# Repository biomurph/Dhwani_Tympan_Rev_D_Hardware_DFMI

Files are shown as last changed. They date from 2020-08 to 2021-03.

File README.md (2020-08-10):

D_Tympan_DFMI_1.0 consisits of PCB design files catering to the requirements of Indian PCB Manufacturers. 

The following are the changes done in the PCB design files (.pcb file):  

	1.Four layered board with power/gnd planes as follows:
		Top Cu - GND plane   
		Second layer(In. Cu 1) - None  
		Third layer(In. Cu 2) - 3.3 V power plane  
		Bottom Cu - GND plane  
	2.Details about vias:  
		Through hole vias - 0.6mm/0.4mm  
		Blind vias ( In. Cu 2 - B. Cu) - 0.45mm/ 0.15mm  
	3. Changes in component placement:  
		R20, R23 - Moved from B. Cu to F. Cu layer  
		C14, C20, C21, C22,C34 - Moved from B. Cu to F. Cu layer

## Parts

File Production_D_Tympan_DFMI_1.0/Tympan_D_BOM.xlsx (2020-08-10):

Item | Reference | Package | Quantity | Value | Manufacturer | Part Number | Notes
1 | BT1 | 4UCON-0217-20519 | 1 | 4UCON-20519 | 4UCON | 20519 | Consigned by Solutions
2 | C1,C3,C5,C7,C10,C14,C16,C18,C28,C29,C42 | C_0402 | 11 | 0.1uF | TDK Corporation | C1005X7R1H104K050BB
3 | C2,C8,C12,C13,C23,C24,C25,C26,C27,C32,C33,C37,C39 | C_0402 | 13 | 2.2uF | Murata | GRT155C71A225KE13D
4 | C30,C31 | C_0402 | 2 | 10nF | Yageo | AC0402KPX7R9BB103
5 | C35 | C_0402 | 1 | 4.7uF | TDK Corporation | C1005X5R1A475K050BC
6 | C4,C6,C11,C15 | C_0402 | 4 | 10uF | Murata | GRM155C80J106ME11J
7 | C40 | C_0402 | 1 | 15pF | Wurth | 885012005008
8 | C41 | C_0402 | 1 | 22nF | Wurth | 885012205014
9 | C9,C17,C19,C20,C21,C22,C34 | C_0402 | 7 | 1uF | Murata | GRM155C81C105KE15D
10 | CONN1 | MOLEX_47571-0001 | 1 | 8_PIN_microSD | Molex | 47571-0001
11 | D1 | ABHB1608S | 1 | 2 color LED | Everlight | 18-225SURSYGC/S530-A4/E4/TR8
12 | D2 | C_1206 | 1 | LED Red | Lite-On | LTST-C150EKT
13 | D3 | C_1206 | 1 | LED Amber | Lite-On | LTST-C150AKT
14 | D4,D5 | ACDBA340-HF | 2 | Shottkey | Comchip | ACDBA340-HF
15 | D6 | CLMVB-FKA-CFHEHLCBB7a363 | 1 | Led_RGB_CA | Cree | CLMVB-FKA-CFHEHLCBB7a363
16 | F1 | C_1206 | 1 | FUSE | Bell Fuse | C1Q 1
17 | IC1 | BGA-144-1mm | 1 | ARM | NXP | MK66FX1M0VMD18
18 | IC2 | QFN-16-1EP_3x3mm_Pitch0.5mm | 1 | MKL02Z32VFG4 | PJRC | IC_MKL02Z32_QFN16 | Consigned by Solutions
19 | IC3 | BC127 | 1 | BC127 | Sierra Wireless | BC127-1103383
20 | J1 | SJ-3523-SMT-TR | 1 | Phone Out | CUI Inc | SJ-3523-SMT-TR
21 | J2 | SJ-3524-SMT-TR | 1 | Mic In | CUI Inc | SJ-3524-SMT-TR-PI
22 | L1,L2 | C_0402 | 2 | 600R | TDK Corporation | MMZ1005S601HT000
23 | L3 | C_0603 | 1 | 1K | Murata | BLM18KG102SH1D
24 | MIC2,MIC1 | SPM0687LR5H-1 | 2 | MEMS Microphone | Knowles | SPM0687LR5H-1
25 | P1 | 10118193_microUSB | 1 | USB_OTG | Amphenol | 10118193-0001LF
26 | P3,P4,P5,P2 | Pin_Header_Straight_1x06_Pitch2.54mm | 4 | CONN_01X06 | Samtec | SSW-106-01-G-S
27 | P6 | Pin_Header_Straight_1x03_Pitch2.00mm | 1 | DNP | DNP | DNP | DNP
28 | R12,R13 | C_0603 | 2 | 0R | Vishay Dale | CRCW06030000Z0EA
29 | R14,R17 | C_0603 | 2 | DNP | DNP | DNP | DNP
30 | R15,R16 | C_0603 | 2 | 2.2K | Yageo | RC0603FR-072K2L
31 | R18,R21 | R_0402 | 2 | 240R | Yageo | RC0402JR-07240RL
32 | R19,R20,R32,R33,R1,R11 | R_0402 | 6 | 1K | Vishay Dale | CRCW04021K00FKED
33 | R23 | R_0402 | 1 | 100K | Vishay Dale | CRCW0402100KFKED
34 | R25,R34,R35,R36 | R_0402 | 4 | 470R | Yageo | RC0402FR-07470RL
35 | R30,R31 | R_0402 | 2 | 10K | Yageo | RC0402FR-0710KL
36 | R6,R2,R3,R4,R5,R7,R9,R10,R26,R27 | R_0402 | 10 | 33R | Yageo | RC0402FR-0733RL
37 | R8 | R_0402 | 1 | 2.2K | Yageo | RC0402JR-0722KL
38 | RV1 | Pin_Header_Straight_1x03_Pitch2.54mm | 1 | POT | Bourns | 3352T-1-103L
39 | SW1 | CL-SB-22A | 1 | Slide Switch | Nidec Copal | CL-SB-22A-11T
40 | SW2 | PTS810 | 1 | TACT_SWITCH | C&K | PTS810 SJK 250 SMTR LFS
41 | U1 | SOT-23-5 | 1 | 3V3 Regulator | Diodes Inc | AP2210K-3.3TRG1
42 | U2 | UQFN-40-1EP_5x5mm_Pitch0.4mm | 1 | CODEC | Texas Instrument | TLV320AIC3206IRSBT
43 | U3 | SOT-353_SC-70-5 | 1 | Analog Switch IC | Texas Instrument | TS5A3166DCKR
44 | U4 | SOT-23-5 | 1 | 1V8 Regulator | Texas Instrument | LP5907MFX-1.8/NOPB
45 | U5 | SOT-23-5 | 1 | LiPo Charge IC | Microchip | MCP73831T-2DCI/OT
46 | Y1 | LFXTAL009678 | 1 | 32.768kHz | IQD | LFXTAL009678Reel
47 | Y2 | FA_238_16.0000MB_K3 | 1 | 16MHz | Epson | FA_238_16.0000MB_K3

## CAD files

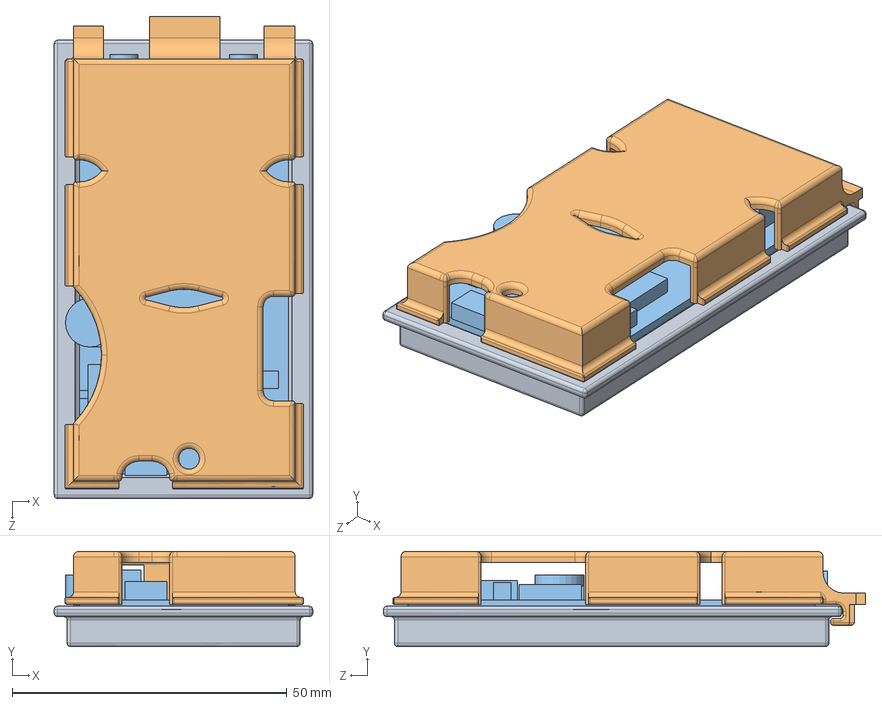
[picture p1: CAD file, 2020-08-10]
Enclosure/Enclosure_01/Tympan D Enclosure Assembly.SLDASM
47.0 x 17.4 x 87.7 mm
Joel Enclosure Bottom
Joel Enclosure Top
Chip's Chip

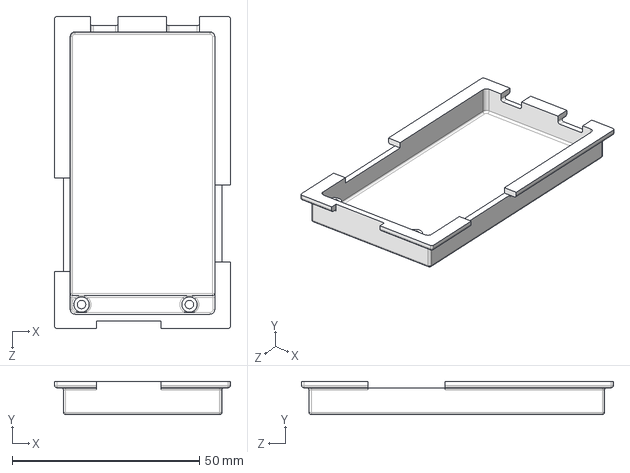
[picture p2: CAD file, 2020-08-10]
DFMI_1.0/Enclosure/Enclosure_01/Tympan D Enclosure Bottom.STEP
47.0 x 8.89 x 83.4 mm

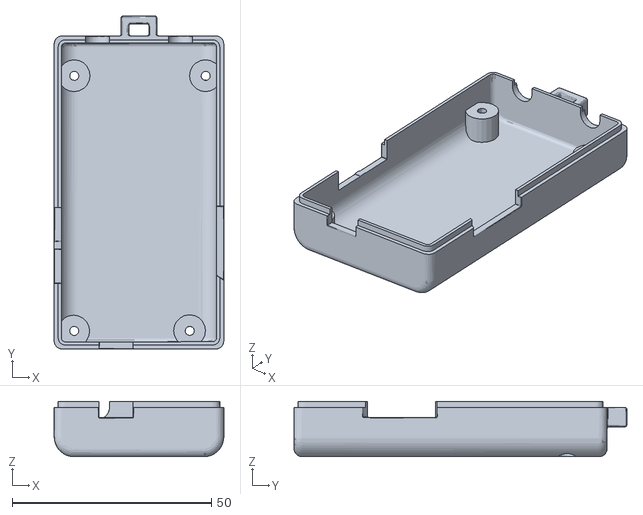
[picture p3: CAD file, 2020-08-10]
Enclosure/Enclosure_02/Tympan RevD Case Bottom.stl
42.6 x 83.6 x 13.9

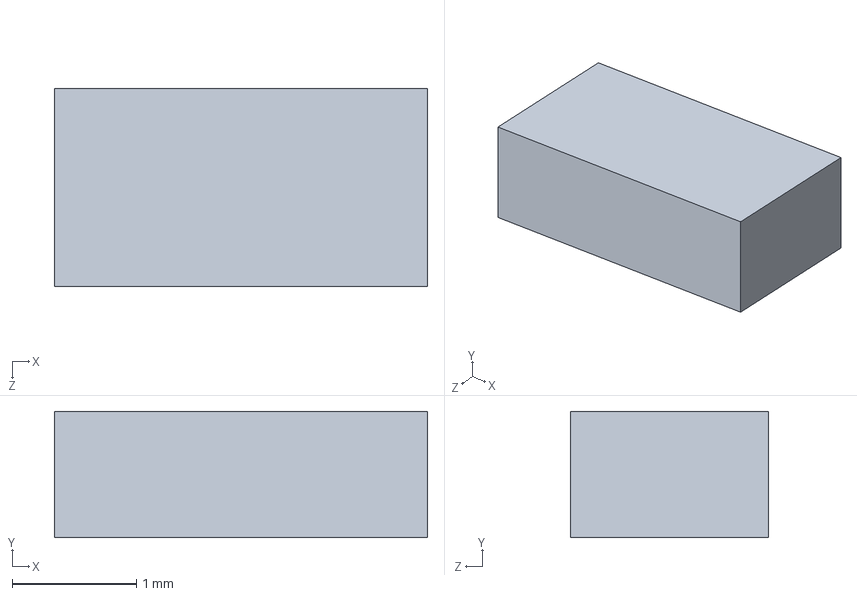
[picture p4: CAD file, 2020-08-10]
Enclosure/PCB ASSY/PCB as ASSY/LED_SMT_GENERIC_FAKE CAD.SLDPRT
3.00 x 1.02 x 1.59 mm

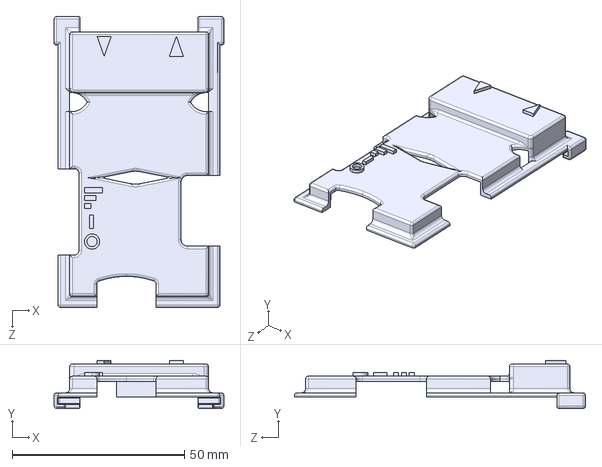
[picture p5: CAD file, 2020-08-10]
DFMI_1.0/Enclosure/Enclosure_01/Tympan D Enclosure Top.STEP
49.3 x 14.0 x 84.5 mm

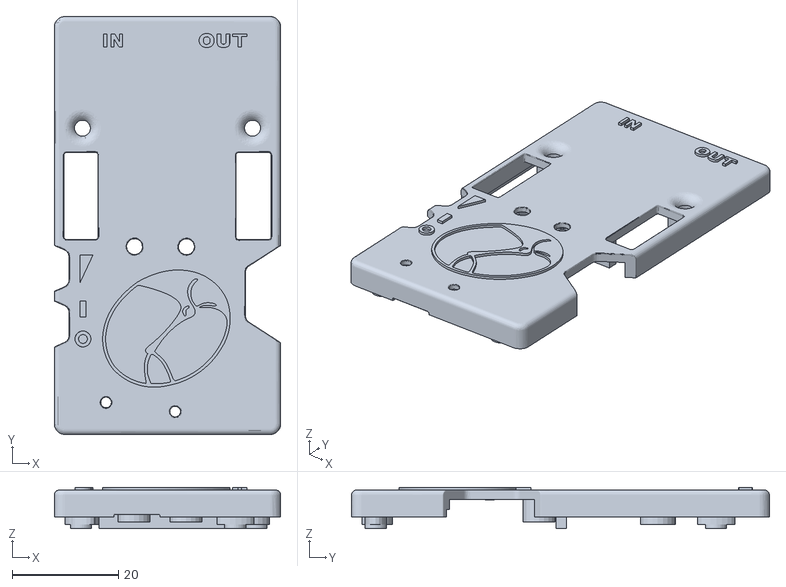
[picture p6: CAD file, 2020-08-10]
Enclosure/Enclosure_02/Tympan RevD Case Top.stl
42.6 x 78.6 x 7.80

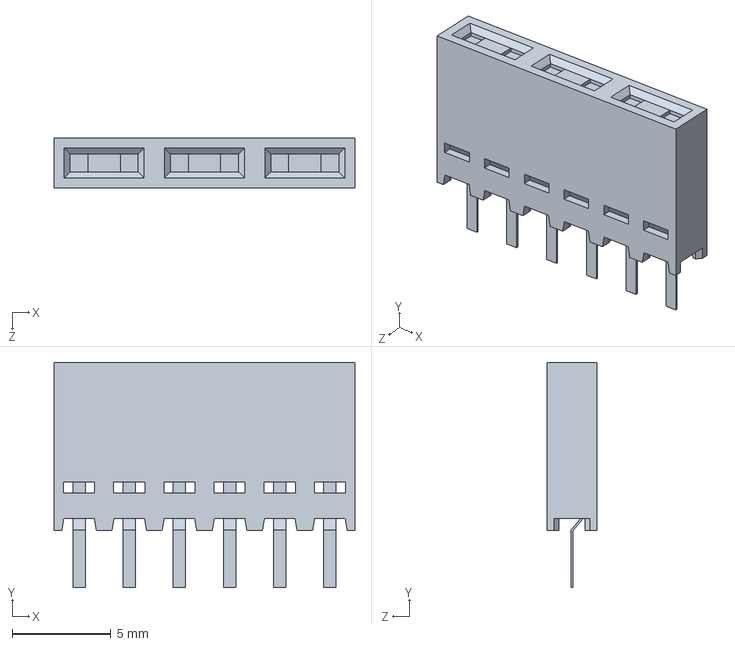
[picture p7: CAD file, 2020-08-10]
Enclosure/PCB ASSY/PCB as ASSY/HEADER_SOCKET_6POS_MOLEX_901471106.SLDPRT
15.2 x 11.4 x 2.54 mm

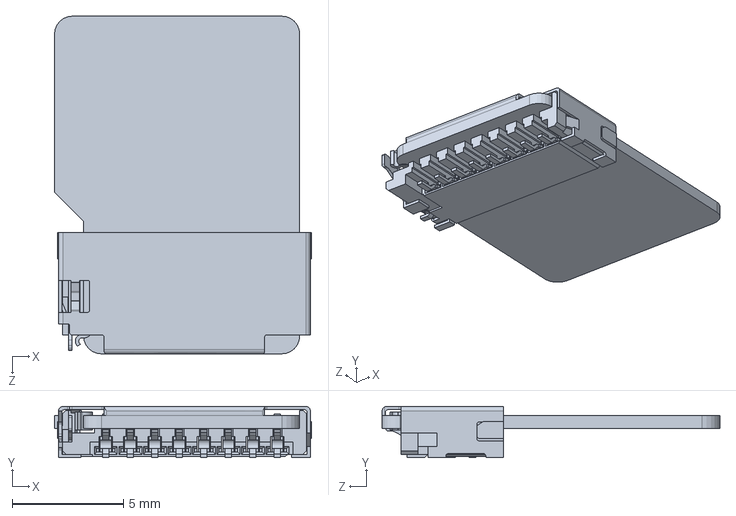
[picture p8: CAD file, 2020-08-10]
Enclosure/PCB ASSY/PCB as ASSY/SD CARD HOLDER_MOLEX_475710001.SLDPRT
11.5 x 2.30 x 15.2 mm

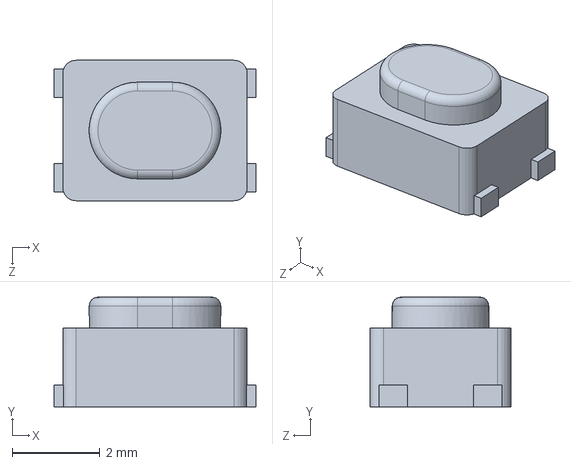
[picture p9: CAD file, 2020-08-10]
Enclosure/PCB ASSY/PCB as ASSY/TACTILE SW_PTS810_CREARE_MOCKUP.SLDPRT
4.60 x 2.50 x 3.20 mm

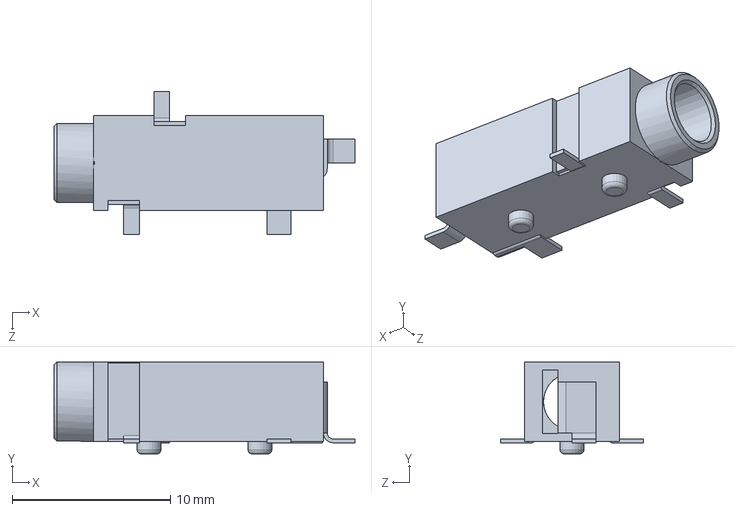
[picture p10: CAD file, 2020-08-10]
Enclosure/PCB ASSY/PCB as ASSY/CUI_DEVICES_SJ-3524-SMT-TR-PI.sldprt
19.0 x 5.80 x 9.00 mm

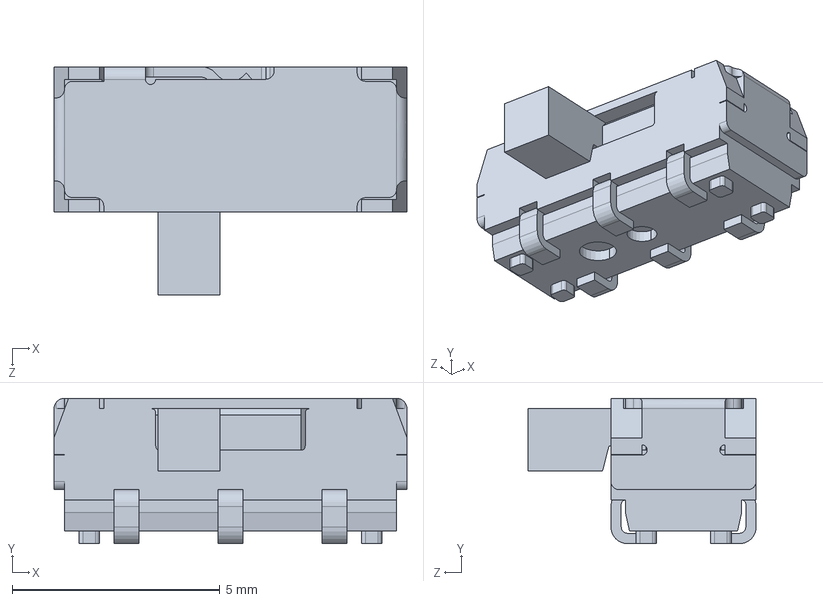
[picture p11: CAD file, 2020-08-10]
Enclosure/PCB ASSY/PCB as ASSY/SWITCH_CL_SB-22A-11T.SLDPRT
8.50 x 3.50 x 5.50 mm

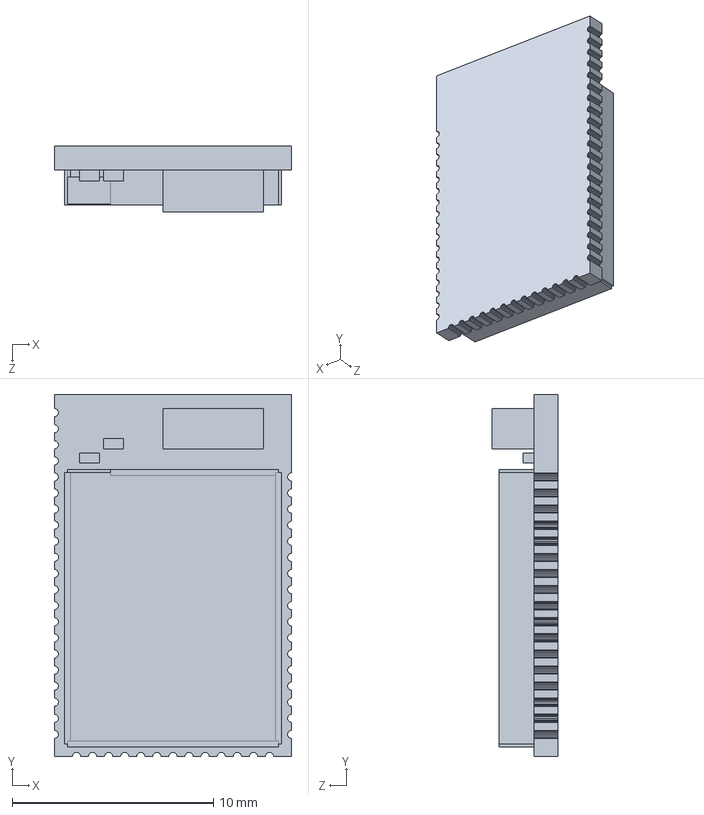
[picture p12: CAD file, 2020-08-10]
Enclosure/PCB ASSY/PCB as ASSY/BT_MODULE_SIERRA_BC127v4x_3.SLDPRT
11.8 x 18.0 x 3.30 mm

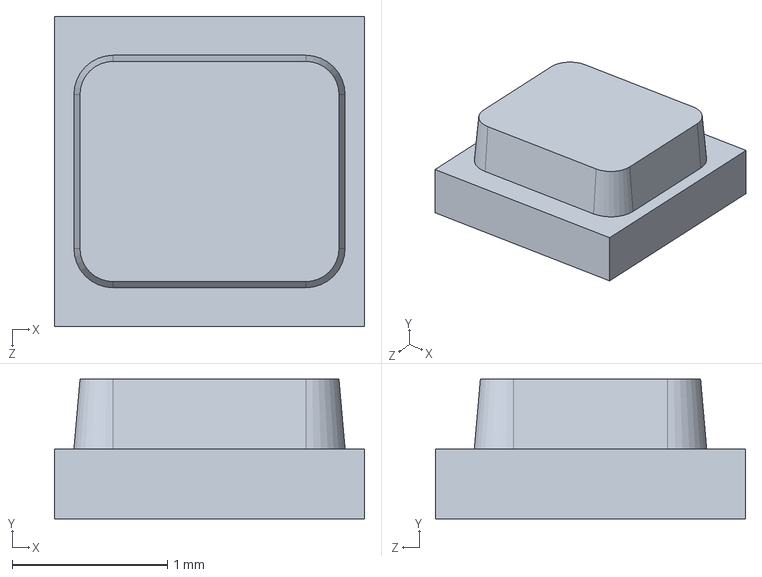
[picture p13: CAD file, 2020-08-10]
Enclosure/PCB ASSY/PCB as ASSY/LED_3COLOR_CREE_CLMVB-FKA-CFHEHLCBB7A363.SLDPRT
2.00 x 0.9 x 2.00 mm

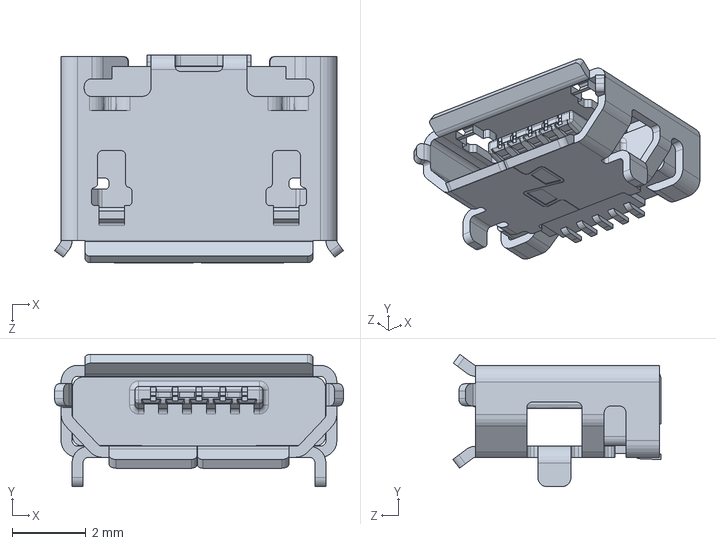
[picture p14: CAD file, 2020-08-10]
Enclosure/PCB ASSY/PCB as ASSY/USB-A_MICRO_10118193-0001lFC.SLDPRT
7.86 x 3.60 x 5.66 mm

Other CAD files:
Enclosure/PCB ASSY/PCB as ASSY/CUI_DEVICES_SJ-3523-SMT-TR.sldprt
Enclosure/PCB ASSY/PCB as ASSY/POTENTIOMETER_BOURNES_3352T-1-103LF.SLDPRT
Enclosure/Enclosure_01/Tympan D Enclosure Bottom.SLDPRT
Enclosure/Enclosure_01/Tympan D Enclosure Bottom.STL
Enclosure/Enclosure_01/Tympan D Enclosure Top.SLDPRT
Enclosure/Enclosure_01/Tympan D Enclosure Top.STL
Enclosure/PCB ASSY/20200131_TYMPAN_PCB_ASSY___SINGLE_PART.SLDPRT
Enclosure/PCB ASSY/PCB as ASSY/20200131_TYMPAN_REV-D_PCB_ASSY.SLDASM

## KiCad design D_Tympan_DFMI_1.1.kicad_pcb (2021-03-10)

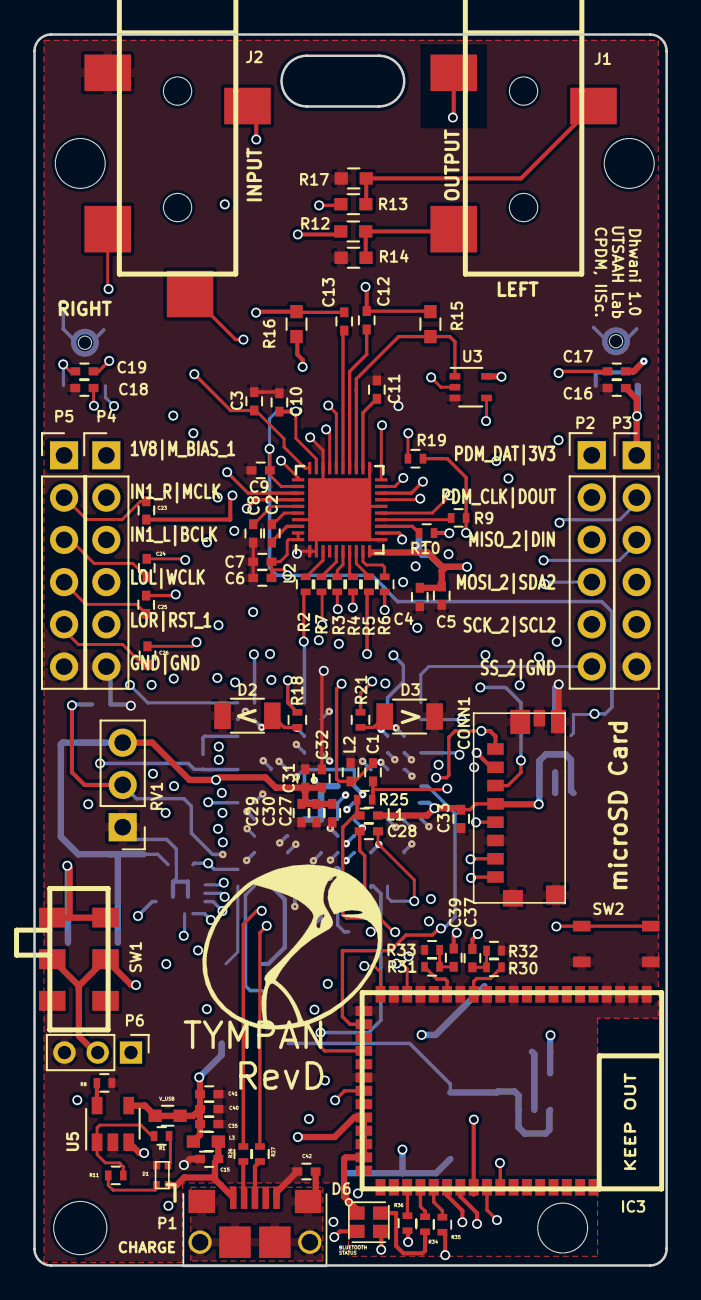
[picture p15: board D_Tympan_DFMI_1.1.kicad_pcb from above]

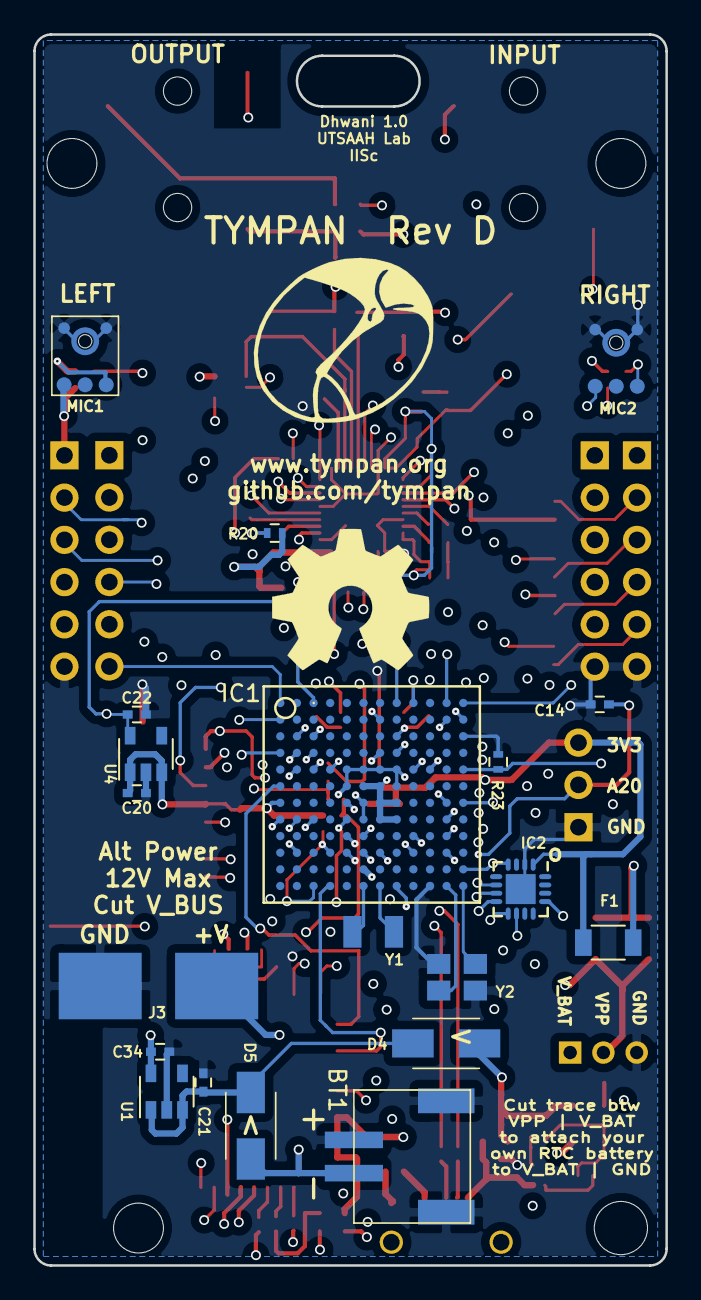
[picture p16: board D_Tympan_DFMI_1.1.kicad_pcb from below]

Board: 4 copper layers, 38.0 x 74.0 mm, 113 parts (20 on the bottom side), 117 nets.

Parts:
BT1: 4UCON-20519; 4UCON-0217-20519
C1, C3, C5, C7, C10, C14, C16, C18, C28, C29, C42: 0.1uF; C_0402
C2, C8, C12, C13, C23, C24, C25, C26, C27, C32, C33, C37, C39: 2.2uF; C_0402
C4, C6, C11, C15: 10uF; C_0402
C9, C17, C19, C20, C21, C22, C34: 1uF; C_0402
C30, C31: 10nF; C_0402
C35: 4.7uF; C_0402
C40: 15pF; C_0402
C41: 22nF; C_0402
CONN1: 8_PIN_microSD; MOLEX_47571-0001
D1: APHB1608SGNC; ABHB1608S
D2, D3: LED; C_1206
D4, D5: Shottkey; ACDBA340-HF
D6: Led_RGB_CA; CLMVB-FKA-CFHEHLCBB7a363
F1: FUSE; C_1206
IC1: MK66FX1M0VMD18; BGA-144-1mm
IC2: MKL02Z32VFG4; QFN-16-1EP_3x3mm_Pitch0.5mm
IC3: BC127
J1: SJ-3523-SMT-TR
J2: SJ-3524-SMT-TR-PI; SJ-3524-SMT-TR
J3: alt Power Pads
L1, L2: 600R; C_0402
L3: 1K; C_0603
MIC1, MIC2: SPM0687LR5H-1
P1: USB_OTG; 10118193_microUSB
P2, P3, P4, P5: CONN_01X06; Pin_Header_Straight_1x06_Pitch2.54mm
P6: CONN_01X03; Pin_Header_Straight_1x03_Pitch2.00mm
P7: CONN_01X01; NPTH_2.4mm
P8, P9, P10: CONN_01X01; NPTH_3.2mm
R1, R11, R19, R20, R32, R33: 1K; R_0402
R2, R3, R4, R5, R6, R7, R9, R10, R26, R27: 33R; R_0402
R8: 2.2K; R_0402
R12, R13: 0R; C_0603
R14, R17: DNP; C_0603
R15, R16: 2.2K; C_0603
R18, R21, R34, R35, R36: 240R; R_0402
R23: 100K; R_0402
R25: 470R; R_0402
R30, R31: 10K; R_0402
RV1: POT; Pin_Header_Straight_1x03_Pitch2.54mm
SW1: CL-SB-22A
SW2: TACT_SWITCH; PTS810
U1: AP2210K-3.3TRG1; SOT-23-5
U2: TLV320AIC3206IRSBT; UQFN-40-1EP_5x5mm_Pitch0.4mm
U3: 74LVC1G66; SOT-353_SC-70-5
U4: LP5907MFX-1.8; SOT-23-5
U5: MCP73831; SOT-23-5
V_USB: DNP; C_0603
Y1: 32.768kHz; LFXTAL009678
Y2: 16MHz; FA_238_16.0000MB_K3

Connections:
+1V8: C6.1, C7.1, C9.1, C10.1, C22.1, P5.1, U2.29, U2.32, U2.39, U2.40, U4.5
+3V3: C3.2, C4.2, C5.2, C16.2, C18.2, C20.1, C27.1, C29.1, C30.1, C31.1, C32.1, C33.1, CONN1.4, D6.1, F1.2, IC1.E5, IC1.E6, IC1.E7, IC1.E8, IC1.F5, IC1.F8, IC1.G1, IC2.1, IC3.30, IC3.31, IC3.32, IC3.33, L1.2, MIC1.4, MIC2.4, P3.1, R19.1, R20.1, RV1.3, U2.10, U2.30, U3.5, U4.1, U4.3
+BATT: BT1.1, D5.2, J3.1, U5.3
/BCLK: IC1.A11, P4.3, R3.1
/BT_CTS: IC1.M8, IC3.40
/BT_PIO0: IC1.F1, IC3.23
/BT_PIO5: IC1.M4, IC3.25
/BT_RTS: IC1.K4, IC3.43
/BT_RX: IC1.E9, IC3.42
/BT_TX: IC1.E10, IC3.41
/BT_nRESET: IC1.K5, IC3.44
/CLK: CONN1.5, IC1.D1
/CMD: CONN1.3, IC1.E4
/DAT0: CONN1.7, IC1.D2
/DAT1: CONN1.8, IC1.D3
/DAT2: CONN1.1, IC1.E2
/DAT3: CONN1.2, IC1.E3
/DIN: IC1.B11, R5.1
/DIN_1: IC1.B12, P3.3
/DOUT: IC1.D8, R6.1
/DOUT_1: IC1.B7, P3.2
/HPL: R12.1, U2.31
/HPR: R13.1, U2.33
/IN1_L: C24.1, C37.1, U2.17
/IN1_R: C23.1, C39.1, U2.18
/IN2_L: C17.1, U2.19
/IN2_R: C19.1, U2.20
/LED_0: IC3.37, R36.1
/LED_1: IC3.38, R34.1
/LED_2: IC3.39, R35.1
/LOL: C25.1, IC3.21, U2.26
/LOR: C26.1, IC3.19, U2.27
/MCLK: IC1.C8, P4.2, R7.1
/MICBIAS: R15.1, U2.23, U3.1
/MICDET: J2.4, U2.34
/MISO_2: IC1.C2, P2.3
/MOSI_2: IC1.C3, P2.4
/M_BIAS: IC1.A3, U3.4
/M_BIAS_1: IC1.H11, P4.1
/PDM_CLK: P2.2, U2.12
/PDM_DAT: P2.1, U2.15
/POT: C14.1, IC1.K11, RV1.2
/PROG: IC2.10, SW2.1, SW2.2
/PTA0: IC1.J5, IC2.8
/PTA1: IC1.J6, IC2.6
/PTA2: IC1.K6, IC2.9
/PTA3: IC1.K7, IC2.7
/RESET_B: IC1.L12, IC2.4, IC2.13
/SCK_2: IC1.B1, P2.5
/SCL2: IC1.K9, P3.5
/SCL/SS: IC1.G12, R10.1, R20.2
/SDA2: IC1.J9, P3.4
/SDA/MOSI: IC1.G11, R9.1, R19.2
/SS_2: IC1.A1, P2.6
/USB: C15.1, D1.3, L3.1, P1.1
/USB0_D+: IC1.H1, R27.2
/USB0_D-: IC1.H2, R26.2
/VREGEN: IC1.E12, IC3.28, R23.1
/V_USB: C35.1, C40.1, C41.1, D4.2, L3.2, U5.4, V_USB.1, V_USB.2
/WCLK: IC1.A12, P4.4, R4.1
/nRESET: IC1.A8, R2.1
/nRESET_1: IC1.J11, P4.5
Earth: C42.2, P1.6, P1.7, P1.8, P1.9, P1.10, P1.11
GND: BT1.2, BT1.3, BT1.4, C3.1, C4.1, C5.1, C6.2, C7.2, C8.2, C9.2, C10.2, C11.2, C14.2, C15.2, C16.1, C18.1, C20.2, C21.2, C22.2, C27.2, C29.2, C30.2, C31.2, C32.2, C33.2, C34.2, C35.2, C40.2, C41.2, C42.1, CONN1.6, CONN1.9, CONN1.10, CONN1.11, CONN1.12, CONN1.13, D1.2, D2.1, D3.1, IC1.C12, IC1.F6, IC1.F7, IC1.G7, IC1.G8, IC1.H3, IC1.H7, IC1.H8, IC1.K2, IC1.M10, IC2.2, IC2.17, IC3.1, IC3.2, IC3.3, IC3.4, IC3.11, IC3.13, IC3.15, IC3.18, IC3.20, IC3.22, IC3.27, J1.1, J2.1, J3.2, L2.2, MIC1.2, MIC1.3, MIC2.2, MIC2.3, P1.5, P3.6, P4.6, P5.6, P6.3, R8.2, R14.2, R17.2, R23.2, R32.2, R33.2, RV1.1, SW2.3, SW2.4, U1.2, U2.1, U2.2, U2.11, U2.16, U2.21, U2.28, U2.37, U2.41, U3.3, U4.2, U5.2, Y2.2, Y2.4
unnamed: C1.1, C28.1, IC1.G6, IC1.H6, L2.1
unnamed: C1.2, IC1.G5, R25.1
unnamed: C2.1, U2.36
unnamed: C2.2, U2.38
unnamed: C8.1, U2.35
unnamed: C11.1, U2.22
unnamed: C12.1, U2.24
unnamed: C12.2, J2.2, R15.2
unnamed: C13.1, U2.25
unnamed: C13.2, J2.3, R16.1
unnamed: C17.2, MIC1.1
unnamed: C19.2, MIC2.1
unnamed: C21.1, D4.1, D5.1, U1.1, U1.3
unnamed: C23.2, P5.2
unnamed: C24.2, P5.3
unnamed: C25.2, P5.4
unnamed: C26.2, P5.5
unnamed: C28.2, IC1.M3
unnamed: C37.2, R30.2, R32.1
unnamed: C39.2, R31.2, R33.1
unnamed: D1.1, R11.1
unnamed: D1.4, R1.1
unnamed: D2.2, R18.2
unnamed: D3.2, R21.2
unnamed: D6.2, R34.2
unnamed: D6.3, R35.2
unnamed: D6.4, R36.2
unnamed: F1.1, SW1.1, SW1.4
unnamed: IC1.A9, R18.1
unnamed: IC1.D7, R21.1
unnamed: IC1.H5, L1.1, R25.2
unnamed: IC1.M6, Y1.1
unnamed: IC1.M7, Y1.2
unnamed: IC1.M11, Y2.1
unnamed: IC1.M12, Y2.3
unnamed: IC3.14, R30.1
unnamed: IC3.16, R31.1
unnamed: J1.2, R12.2, R14.1
unnamed: J1.3, R13.2, R17.1
unnamed: P1.2, R26.1
unnamed: P1.3, R27.1
unnamed: R1.2, R11.2, U5.1
unnamed: R2.2, U2.3
unnamed: R3.2, U2.6
unnamed: R4.2, U2.7
unnamed: R5.2, U2.8
unnamed: R6.2, U2.9
unnamed: R7.2, U2.5
unnamed: R8.1, U5.5
unnamed: R9.2, U2.14
unnamed: R10.2, U2.13
unnamed: R16.2, U3.2
VPP: C34.1, IC1.L6, P6.1, P6.2, SW1.2, SW1.5, U1.5

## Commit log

2020-05-01 DMF changes for HiQ electronics bangalore
    DMF changes for HiQ electronics bangalore
    [Tympan_D.kicad_pcb]
2020-05-06 Updated the gerber files for DFMI
    [Tympan_D-B.Cu.gbr, Tympan_D-B.Mask.gbr, Tympan_D-B_Cu.gbr, Tympan_D-B_Mask.gbr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]
2020-08-10 Added DFMI_1.0
    [20200131_TYMPAN_PCB_ASSY___SINGLE_PART.SLDPRT, 20200131_TYMPAN_REV-D_PCB_ASSY.SLDASM, BT_MODULE_SIERRA_BC127v4x_3.SLDPRT, CUI_DEVICES_SJ-3523-SMT-TR.sldprt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]
2020-08-10 Changes in DFMI1.0
    [20200131_TYMPAN_PCB_ASSY___SINGLE_PART.SLDPRT, 20200131_TYMPAN_REV-D_PCB_ASSY.SLDASM, BT_MODULE_SIERRA_BC127v4x_3.SLDPRT, CUI_DEVICES_SJ-3523-SMT-TR.sldprt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]
2020-08-13 Added some notes on the PCB board file
    This looks basically OK. I would 'soften' some of the traces where you have almost right angles in them, but that may be more asthetic. Please see the notes I have put on the Eco2.Use layer in the bo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
    [D_Tympan_DFMI_1.0.kicad_pcb]
2020-08-13 final save on the changes
    [D_Tympan_DFMI_1.0.kicad_pcb]
2021-03-04 Add files via upload
    Responses to review comments:
    Updated the annual ring to the Gnd net.
    Extended the zone outline of In.2Cu towards board outline to ensure continuity in the Copper pour.
    [D_Tympan_DFMI_1.1.kicad_pcb]
2021-03-04 Add files via upload
    1. Updated the annual ring in both the microphones to GND net.
    2. Extended the zone outline of In.2 Cu (3.3 V) towards the board outline to ensure connectivity in the Copper pour.
    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
    [D_Tympan_DFMI_1.1.kicad_pcb]
